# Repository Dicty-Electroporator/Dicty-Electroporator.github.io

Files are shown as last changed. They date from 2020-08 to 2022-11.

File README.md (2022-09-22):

<h2>
   <p><em>Dictyostelium</em> <em>discoideum</em> Electroporator</p>
</h2>
<p><a href="https://minhaskamal.github.io/DownGit/#/home?url=https://github.com/Dicty-Electroporator/Dicty-Electroporator.github.io/tree/Gen-2.1-with-edits/Dictyostelium%20discoideum%20Electroporator">Download Project</a></p>
<p>Easily constructed by investigators with no electronics knowledge, we present an inexpensive and open-source electroporation apparatus for <em>Dictyostelium discoideum</em> with all functional modules and peripherals from Cauchy et al., 2022, "A Low-cost Electroporator for Genetically Modifying Social Amoeba <em>Dictyostelium discoideum</em>" submitted to Journal of Open Hardware.</p>
<p><strong>Description:&nbsp;</strong>Electroporation to introduce DNA into cells is a common technique in genetic engineering. <em>Dictyostelium discoideum</em> is a well-established eukaryotic model organism that is frequently genetically modified (transformed). We present here an electroporator capable of high efficiency transformation. Our electroporator consists of a high voltage power supply, pulse generator circuit and cell sample cuvette chamber. The power supply is programmed to deliver desired voltage, which when activated by a double-pole, double-throw switch (DPDT) charges a capacitor. Further switching allows the charged capacitor to deliver a precise, consistent exponential decay wave of the proper duration to the cuvette containing a <em>D. discoideum</em> cell and DNA mixture. The high-voltage circuit is housed in an electrically insulated enclosure - we chose a plastic electrical junction box with appropriate holes for switch mounting and cables to pass. A 3D printable cuvette holder was designed and is available in .stl, .dwg and .iges formats. An inexpensive 1,000-volt digital multimeter was integrated into the design to aid in development and testing. To provide hands-free monitoring of the real-time capacitor voltage, we connected multimeter test leads to the capacitor poles. In addition to the standard build, we present here an alternative design for the pulse generator, which we will refer to as "modular". The standard pulse generator was designed to be durable for repeated use in multiple <em>D. discoideum</em> electroporation experiments. This design includes a soldered padboard with high power rated components. The modular pulse generator is designed for ease of build, is easily modified by swapping components for alternative waveforms, and is intended for a small number of electroporations and not routine or repeated use.</p>

<p><strong>License:&nbsp;</strong><a href="https://minhaskamal.github.io/DownGit/#/home?url=https://github.com/Dicty-Electroporator/Dicty-Electroporator.github.io/blob/Base/LICENSE">CERN Open Hardware License</a></p>
<p>&nbsp;</p> 
<h1>
   <p><em>D. discoideum</em> Electroporation System</p>
</h1>
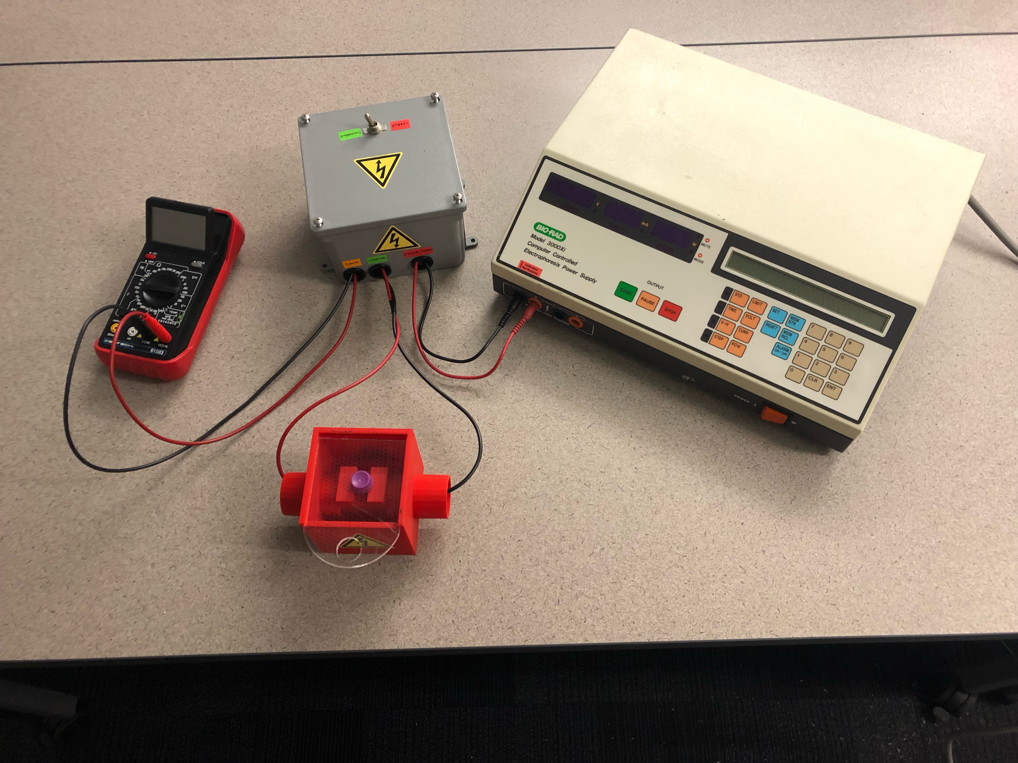
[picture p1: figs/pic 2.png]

<h2>
   <p>Standard Pulse Generator</p>
</h2>
<p>The pulse generator circuit features a soldered breadboard with high power components. Assembly is straightforward and can be constructed by a beginner with access to soldering equipment. The cuvette chamber features a built-in enclosure with limited access to the power connectors as well as a removable lid. The lid can be 3D printed or laser cut from a sheet of acrylic or other material. 3D design and print files are available on this page. We chose a biodegradable and fire-resistant 3D print media,  Polylactic acid (PLA). Other cost effective, readily available, and more durable print media are available. The system was tested and performs as efficiently as a commercial electroporator.</p>
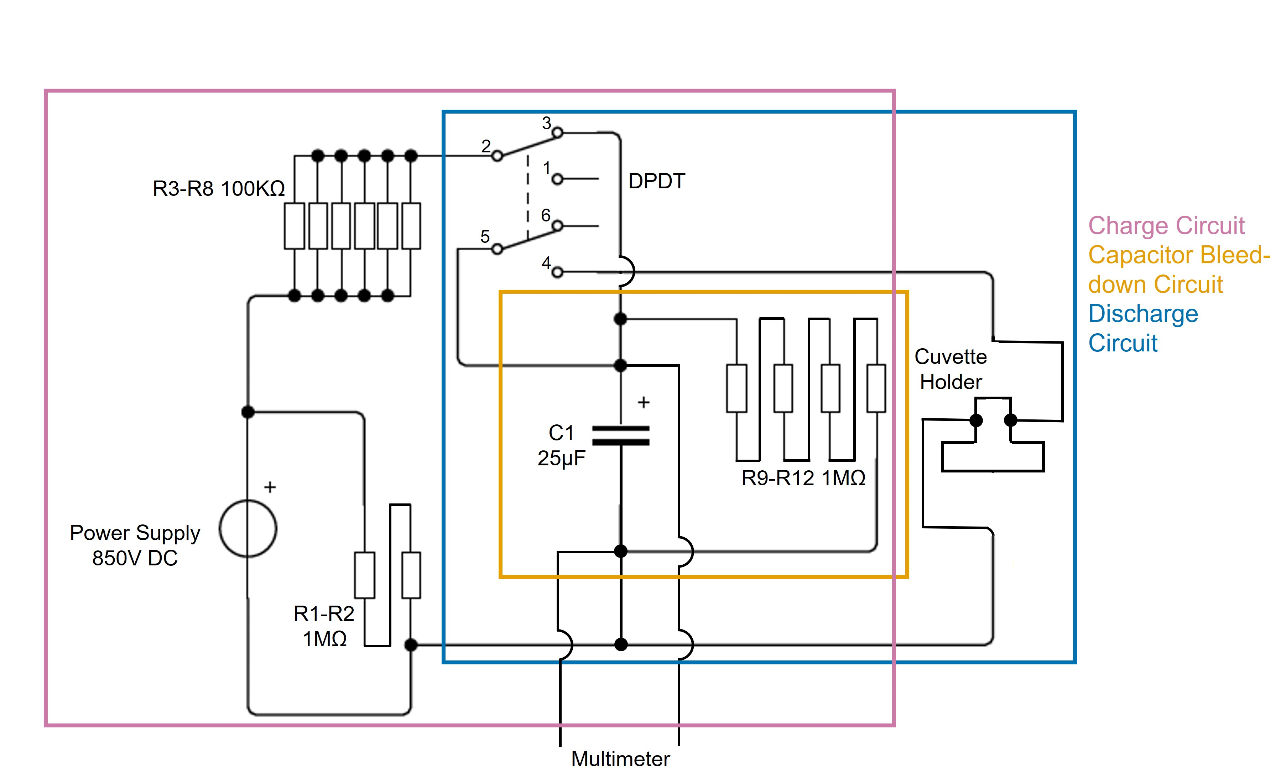
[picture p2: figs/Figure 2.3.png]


<p>2W (Watt)-1MΩ (Ohm) resistors were used for resistors R1-R2 and R9-R12. 8W-100kΩ resistors were used for resistors R3-R8.</p>
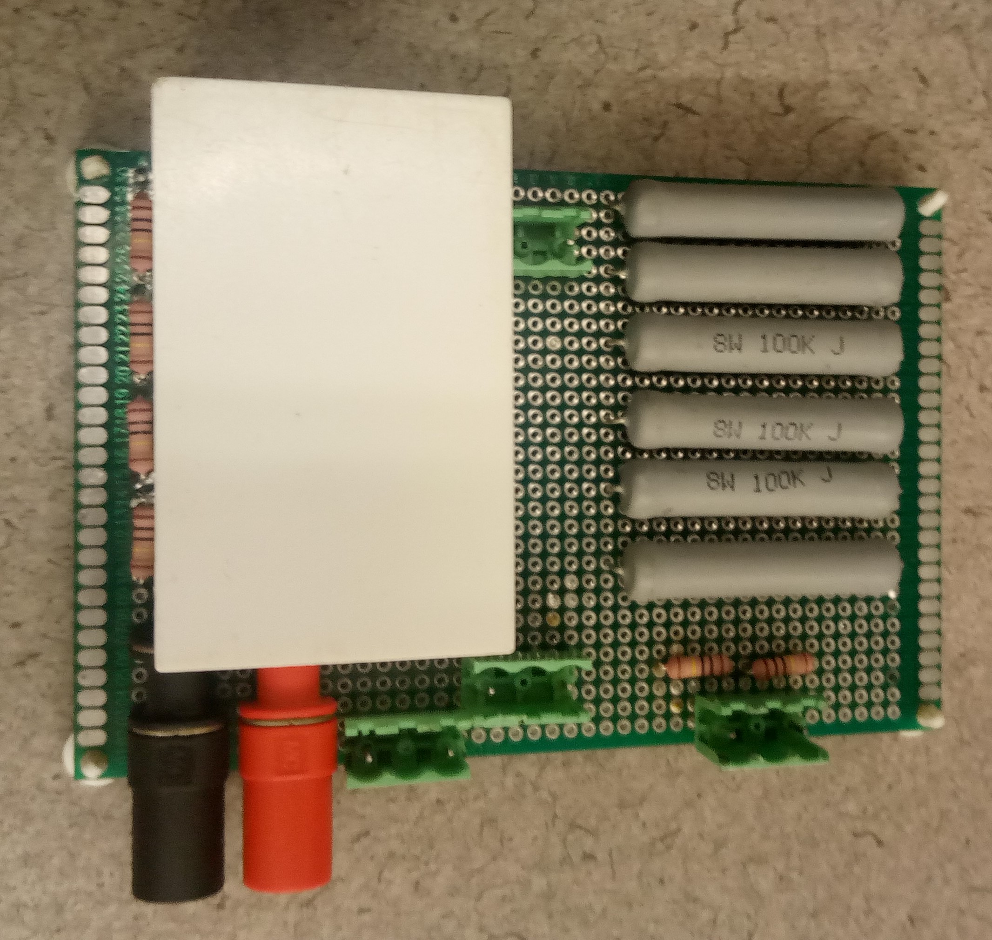
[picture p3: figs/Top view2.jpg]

<p>&nbsp;</p>
<p>Components were fixed to the breadboard using the long leads of resistors as traces on the underside of the 8cm x 12cm padboard.</p>
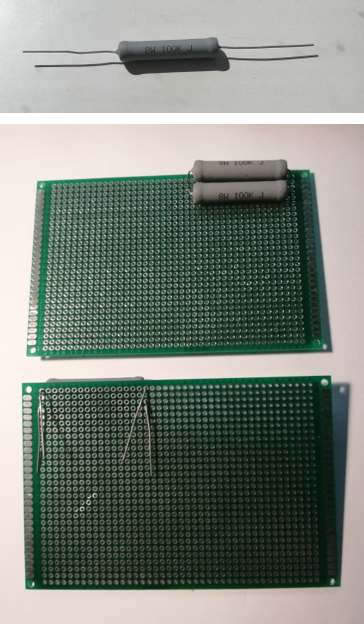
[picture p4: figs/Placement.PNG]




<p>Trimmed resistor terminals and solder were used to create traces. This layout accommodates the lack of premade traces found on solderless breadboards. In addition, banana jack connectors were soldered to the component side and traced to the opposing capacitor poles at each end of the bleed-down resistor array. This allows connection to a multimeter and real-time monitoring of the capacitor voltage during electroporation and provides assurance the capacitor is safe.</p>
<h2>
   <p>Enclosure</p>
</h2>
<p>We chose a commercially available plastic junction box to enclose our pulse generator circuit. A 13mm hole was drilled into the enclosure cover for the DPDT and 22mm holes were marked and drilled in the enclosure which provided a nice fit for the plastic NM connectors and pass-through cables.</p>
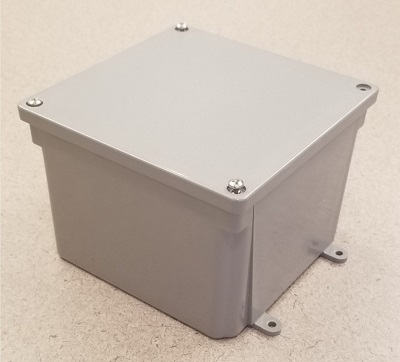
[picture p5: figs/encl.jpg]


<h4>
   <p>Assembly instruction</p>
</h4>
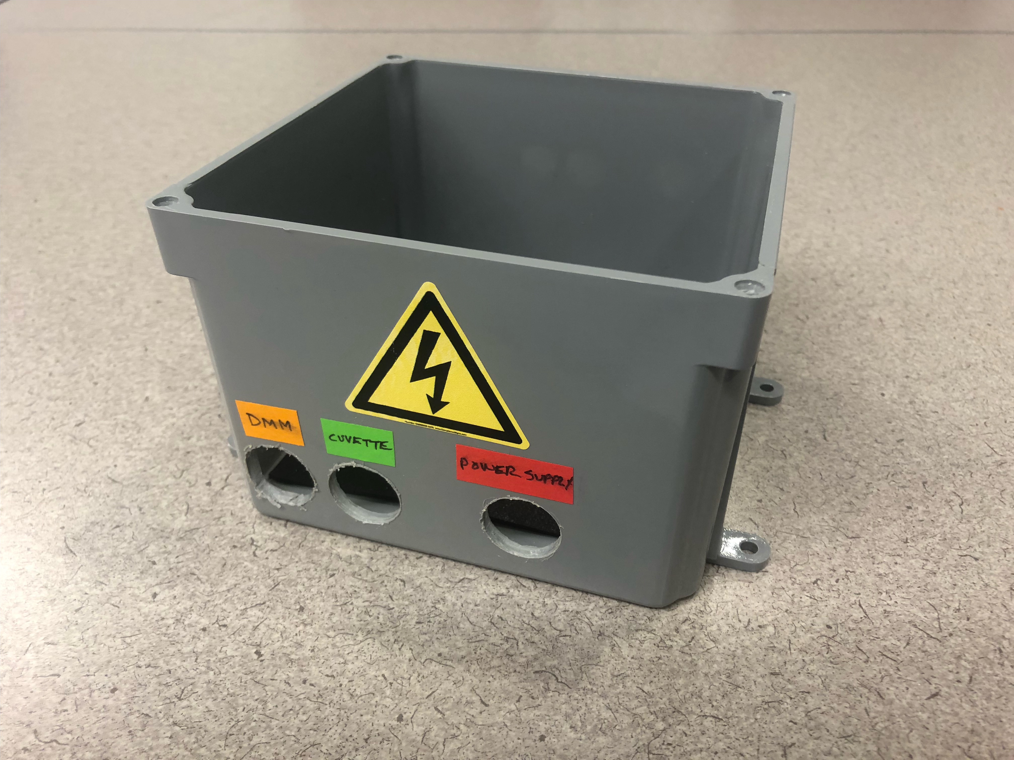
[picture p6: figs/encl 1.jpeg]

<p>Drill three 22mm holes in any side of the enclosure. Label the holes as shown. DMM above refers to digital multimeter.</p>
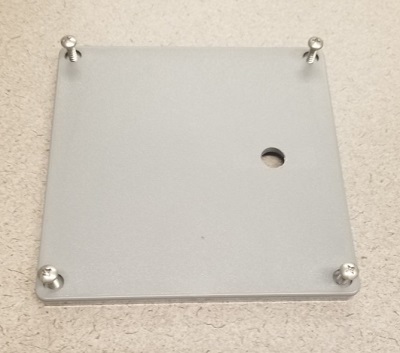
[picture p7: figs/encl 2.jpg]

<p>Drill 13mm hole in enclosure lid for switch mounting. Place the hole where hand-switching will be most comfortable.</p>
<p>&nbsp;</p>
<h3>
   <p>Switch wiring</p>
</h3>
<p>&nbsp;</p>
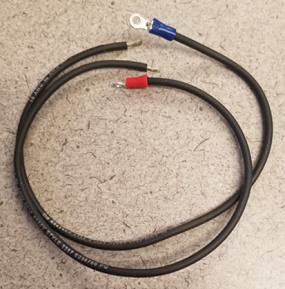
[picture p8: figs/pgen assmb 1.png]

<p>Cut 4 pieces of 18 AWG wire (for the switch) to 30cm lengths and strip approx. 5mm of bare wire from each end. Crimp one end of each wire to a ring terminal.</p>
<p>&nbsp;</p>
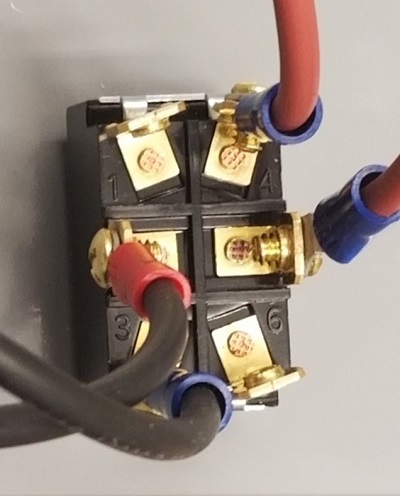
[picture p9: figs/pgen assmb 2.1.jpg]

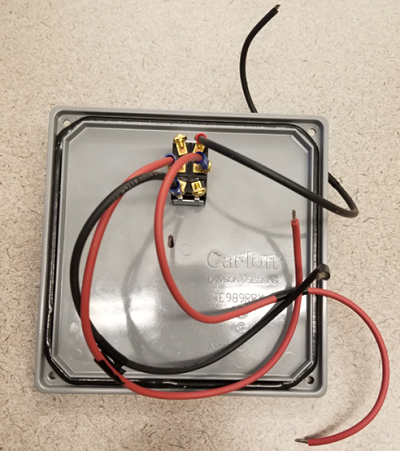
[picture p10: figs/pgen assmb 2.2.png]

<p>Attach ring terminals (with wire from step 1) to terminals 2, 3, 4, and 5 of the DPDT switch. Install switch into hole drilled into lid of case.</p>
<p>&nbsp;</p>
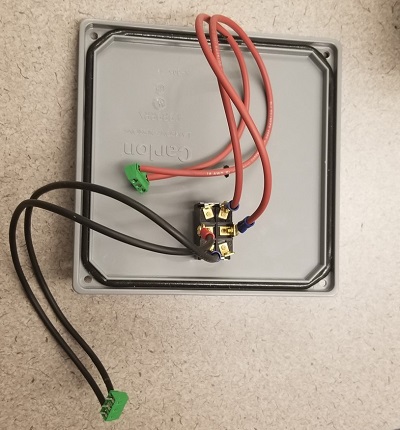
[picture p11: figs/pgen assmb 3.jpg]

<p>Using the 4 pieces of 18 AWG wire with ring terminals from step 1, connect switch terminals 2 and 3 to the outboard ports of one terminal block and 4 and 5 to the outboard ports of another terminal block. Insert paired wires into outside wire cages of terminal blocks, then tighten terminal block screws.</p>
<p>&nbsp;</p>
<h2>
   <p>Cuvette Chamber</p>
</h2>
<p>The cuvette chamber provides the delivery vehicle for the electric field that causes electroporation. The cuvette chamber was designed to keep inward pressure on the plug ends that contact the cuvette. Hands-free electroporation was an important consideration in our design. The built-in spring-like nature of the resulting connection ensures constant contact when like charges build up on each plug and its corresponding cuvette contact. It is also notable that we chose stackable banana plugs so that we could tandem a 1,000V multimeter to the cuvette holder; especially useful during pre-electroporation functions check.</p>

<p>The cuvette chamber has several safety features. It is enclosed in a four-sided box with a removable lid that can be laser cut from a clear Poly acrylic sheet or 3D printed. Collars around lead connectors provide protection from shock exposure. Design and print files are included below. The chamber can be printed with various levels of fill; 15% fill is shown here and functioned well in our hands.</p>
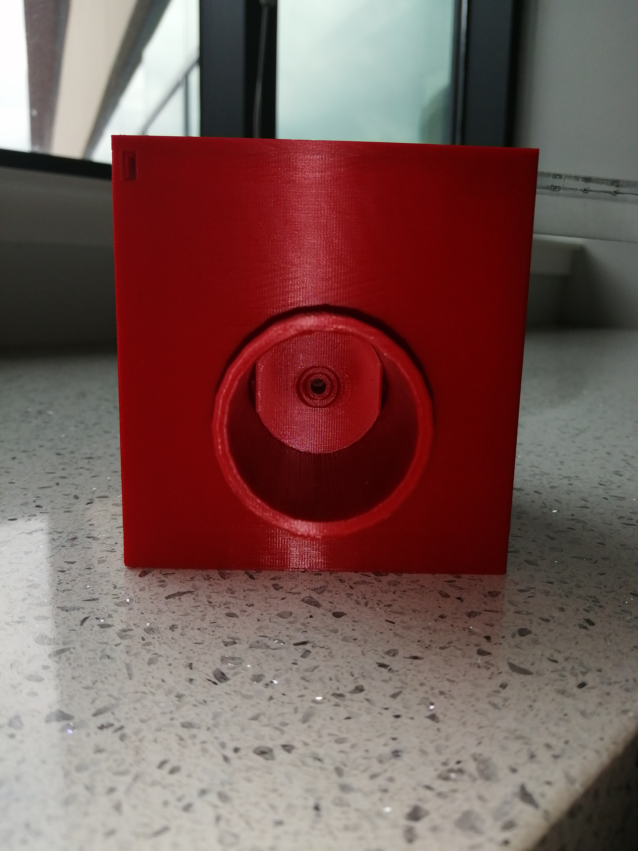
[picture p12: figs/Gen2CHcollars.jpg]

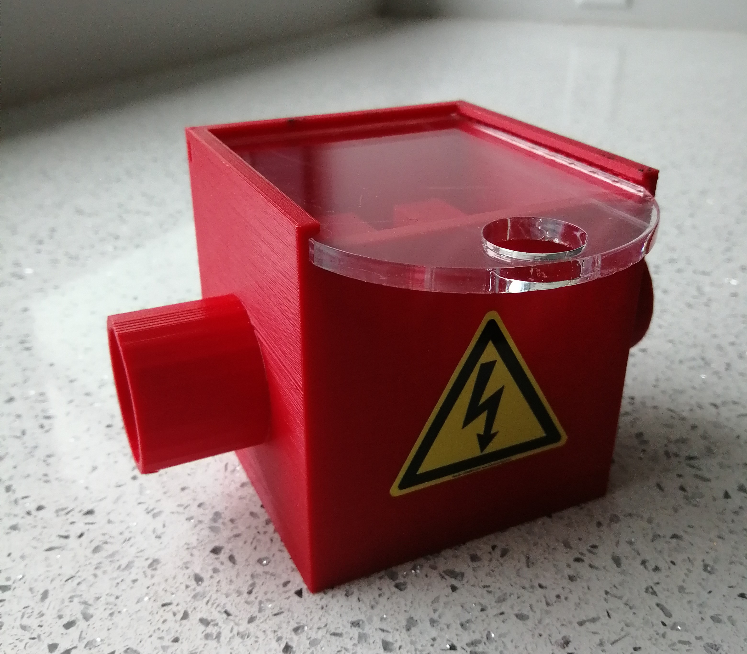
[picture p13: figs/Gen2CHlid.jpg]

<p><strong>Print File:&nbsp;<a href="https://github.com/Dicty-Electroporator/Dicty-Electroporator.github.io/raw/Gen-2.1-with-edits/Enhanced%20Cuvette%20Chamber%203DPrintSTL.stl">Cuvette Chamber.stl</a></strong></p>
<p><strong>CAD Design File:&nbsp;<a href="https://github.com/Dicty-Electroporator/Dicty-Electroporator.github.io/raw/Gen-2.1-with-edits/Enhanced%20Cuvette%20Chamber%20CAD.dwg">Cuvette Chamber CAD.dwg</a></strong></p>
<p><strong>IGES File:&nbsp;<a href="https://minhaskamal.github.io/DownGit/#/home?url=https://github.com/Dicty-Electroporator/Dicty-Electroporator.github.io/blob/Gen-2.1-with-edits/Dictyostelium%20discoideum%20Electroporator/Enclosure%20Lid%20FreeCAD.iges">Cuvette Chamber.iges</a></strong></p>

<p><strong>Chamber Lid Laser Cut File:&nbsp;<a href="https://github.com/Dicty-Electroporator/Dicty-Electroporator.github.io/raw/Gen-2.1-with-edits/Enclosure%20Lid%20LaserCutSVG.svg">Chamber Lid.SVG</a></strong></p>
<p><strong>Chamber Lid Print File:&nbsp;<a href="https://github.com/Dicty-Electroporator/Dicty-Electroporator.github.io/raw/Gen-2.1-with-edits/Enclosure%20Lid%20STL.stl">Chamber Lid STL.stl</a></strong></p>
<p><strong>Chamber Lid CAD Design File:&nbsp;<a href="https://github.com/Dicty-Electroporator/Dicty-Electroporator.github.io/raw/Gen-2.1-with-edits/Enclosure%20Lid%20CAD.dwg">Chamber Lid CAD.dwg</a></strong></p>

<p><strong>Chamber Lid IGES File:&nbsp;<a href="https://minhaskamal.github.io/DownGit/#/home?url=https://github.com/Dicty-Electroporator/Dicty-Electroporator.github.io/blob/Gen-2.1-with-edits/Dictyostelium%20discoideum%20Electroporator/Enhanced%20Cuvette%20Chamber%20FreeCAD.iges">Chamber Lid.iges</a></strong></p>
<p>Note: IGES drawing files save vector image data to transfer information between different CAD applications. Graphics acceleration may have to be disabled in order for some open source CAD software to load.</p>
<p>&nbsp;</p>
<h2>
   <p>Bill of Materials</p>
</h2>
<table>
   <thead>
      <tr>
         <td>
            <p><strong>Part</strong></p>
         </td>
         <td>
            <p><strong>Quantity</strong></p>
         </td>
         <td>
            <p><strong>Supplier</strong></p>
         </td>
         <td>
            <p><strong>Supplier part number</strong></p>
         </td>
         <td>
            <p><strong>URL</strong></p>
         </td>
      </tr>
   </thead>
   <tbody>
      <tr>
         <td>
            <p>Power supply banana plug test leads</p>
         </td>
         <td>
            <p>2</p>
         </td>
         <td>
            <p>Mouser</p>
         </td>
         <td>
            <p>4911A-60/4911A-62</p>
         </td>
         <td>
            <p><a href="https://www.mouser.com/Search/Refine?Keyword=4911a-60">www.mouser.com</a></p>
         </td>
      </tr>
          <tr>
         <td>
            <p>Test Lead Wire 25 in. red</p>
         </td>
         <td>
            <p>1</p>
         </td>
         <td>
            <p>Powerwerx</p>
         </td>
         <td>
            <p>Wire-TL-18-00-25</p>
         </td>
         <td>
            <p><a href="https://powerwerx.com/test-lead-rubber-flexible-wire">powerwerx.com</a></p>
         </td>
      </tr>
      <tr>
         <td>
            <p>Test Lead Wire 25 in. black</p>
         </td>
         <td>
            <p>1</p>
         </td>
         <td>
            <p>Powerwerx</p>
         </td>
         <td>
            <p>Wire-TL-18-00-25</p>
         </td>
         <td>
            <p><a href="https://powerwerx.com/test-lead-rubber-flexible-wire">powerwerx.com</a></p>
         </td>
      </tr>
      <tr>
         <td>
            <p>PCB Prototype padboard - 8cm x 12cm</p>
         </td>
         <td>
            <p>1</p>
         </td>
         <td>
            <p>Amazon</p>
         </td>
         <td>
            <p>739340318574</p>
         </td>
         <td>
            <p><a href="https://www.amazon.com/gp/product/B07Y3DVM1W/ref=ppx_yo_dt_b_asin_title_o05_s00?ie=UTF8&psc=1">www.amazon.com</a></p>
         </td>
      </tr>
      <tr>
         <td>
            <p>Resistors - 8W-100kΩ</p>
         </td>
         <td>
            <p>6</p>
         </td>
         <td>
            <p>Mouser</p>
         </td>
         <td>
            <p>279-ROX8J100K</p>
         </td>
         <td>
            <p><a href="https://www.mouser.com/ProductDetail/TE-Connectivity-Holsworthy/ROX8J100K?qs=gZXFycFWdAMYKZPoGrub8g%3D%3D">www.mouser.com</a></p>
         </td>
      </tr>
      <tr>
         <td>
            <p>Resistors - 2W-1MΩ</p>
         </td>
         <td>
            <p>6</p>
         </td>
         <td>
            <p>Mouser</p>
         </td>
         <td>
            <p>594-5083NW1M000J</p>
         </td>
         <td>
            <p><a href="https://www.mouser.com/ProductDetail/Vishay-BC-Components/PR02000201004JR500?qs=LCMWAU1DZcwmgZ1lvVsGww%3D%3D">www.mouser.com</a></p>
         </td>
      </tr>
      <tr>
         <td>
            <p>Bio-Rad Model 3000xi Computer Controlled Electrophoresis Power Supply (or similar capable of generating at least 1KV DC)</p>
         </td>
         <td>
            <p>1</p>
         </td>
         <td>
            <p>ebay or other supplier of used scientific equipment</p>
         </td>
         <td>
            
         </td>
         <td>
            <p><a href="https://www.ebay.com">www.ebay.com</a></p>
         </td>
      </tr>
      <tr>
         <td>
            <p>3-Pin 5.08mm Pitch Male Female Plug-in PCB Screw Terminal Block Connector</p>
         </td>
         <td>
            <p>2</p>
         </td>
         <td>
            <p>Amazon</p>
         </td>
         <td>
            <p>0766832280286</p>
         </td>
         <td>
            <p><a href="https://www.amazon.com/PoiLee-5-08mm-Female-Terminal-Connector/dp/B07TQLYQ7W/ref=asc_df_B07TQLYQ7W/?tag=hyprod-20&linkCode=df0&hvadid=385629037133&hvpos=&hvnetw=g&hvrand=8172029133657464055&hvpone=&hvptwo=&hvqmt=&hvdev=c&hvdvcmdl=&hvlocint=&hvlocphy=9005131&hvtargid=pla-846156762614&psc=1&tag=&ref=&adgrpid=73872201970&hvpone=&hvptwo=&hvadid=385629037133&hvpos=&hvnetw=g&hvrand=8172029133657464055&hvqmt=&hvdev=c&hvdvcmdl=&hvlocint=&hvlocphy=9005131&hvtargid=pla-846156762614">www.amazon.com</a></p>
         </td>
      </tr>
      <tr>
         <td>
            <p>3-Position Screw Terminal Block</p>
         </td>
         <td>
            <p>2</p>
         </td>
         <td>
            <p>Addicore</p>
         </td>
         <td>
            <p>AD305</p>
         </td>
         <td>
            <p><a href="https://www.addicore.com/3-Position-Screw-Terminal-Block-p/ad305.htm">www.addicore.com</a></p>
         </td>
      </tr>
      <tr>
         <td>
            <p>Male-Male fixed length jumper wires</p>
         </td>
         <td>
            <p>5</p>
         </td>
         <td>
            <p>Jameco</p>
         </td>
         <td>
            <p>2127718</p>
         </td>
         <td>
            <p><a href="https://www.jameco.com/z/WJW-70B-5-70-Piece-Jumper-Wire-Kit-22AWG-14-Lengths-10-Colors_2127718.html">www.jameco.com</a></p>
         </td>
      </tr>

      <tr>
         <td>
            <p>Capacitor - 25μF - 1,300V</p>
         </td>
         <td>
            <p>1</p>
         </td>
         <td>
            <p>Mouser</p>
         </td>
         <td>
            <p>C4AQUBW5250A3NJ</p>
         </td>
         <td>
            <p><a href="https://www.mouser.com/ProductDetail/KEMET/C4AQUBW5250A3NJ?qs=%2Fha2pyFadugKSuBjMOjke5u9ridkq4YeClSJSpnddrBZ2GZPnEOejQ%3D%3D">www.mouser.com</a></p>
         </td>
      </tr>

      <tr>
         <td>
            <p>Ring Terminals</p>
         </td>
         <td>
            <p>4</p>
         </td>
         <td>
            <p>Lowes</p>
         </td>
         <td>
            <p>136093</p>
         </td>
         <td>
            <p><a href="https://www.lowes.com/pd/Utilitech-20-Count-Ring-Wire-Connectors/999953294">www.lowes.com</a></p>
         </td>
      </tr>

      <tr>
         <td>
            <p>DPDT toggle switch - 20A</p>
         </td>
         <td>
            <p>1</p>
         </td>
         <td>
            <p>Ace Hardware</p>
         </td>
         <td>
            <p>GSW-16</p>
         </td>
         <td>
            <p><a href="https://www.acehardware.com/departments/lighting-and-electrical/switches-outlets-and-plugs/switches/3531324">www.acehardware.com</a></p>
         </td>
      </tr>
      <tr>
         <td>
            <p>3/8-in Plastic NM Connector</p>
         </td>
         <td>
            <p>2</p>
         </td>
         <td>
            <p>Lowes</p>
         </td>
         <td>
            <p>44740</p>
         </td>
         <td>
            <p><a href="https://www.lowes.com/pd/Sigma-Electric-ProConnex-3-8-in-Snap-in-Connector-Conduit-Fitting/3151125">www.lowes.com</a></p>
         </td>
      </tr>
      <tr>
         <td>
            <p>Junction box</p>
         </td>
         <td>
            <p>1</p>
         </td>
         <td>
            <p>Lowes</p>
         </td>
         <td>
            <p>10029</p>
         </td>
         <td>
            <p><a href="https://www.lowes.com/pd/CANTEX-Junction-Box-Gang-Gray-Plastic-Weatherproof-New-Work-Old-Work-Standard-Square-Interior-Exterior-Electrical-Box/3276255">www.lowes.com</a></p>
         </td>
      </tr>
      <tr>
         <td>
            <p>3D printed cuvette holder</p>
         </td>
         <td>
            <p>1</p>
         </td>
         <td>&nbsp;</td>
         <td>&nbsp;</td>
         <td>&nbsp;</td>
      </tr>
      <tr>
         <td>
            <p>1kV Multimeter</p>
         </td>
         <td>
            <p>1</p>
         </td>
         <td>
            <p>CEN-TECH (or similar)</p>
         </td>
         <td>
            <p>61593/P37772</p>
         </td>
         <td>
            <p><a href="https://www.harborfreight.com/11-function-digital-multimeter-with-audible-continuity-61593.html">www.harborfreight.com</a></p>
         </td>
      </tr>

      <tr>
         <td>
            <p>Banana Jack Connector Standard Banana Solder Red/Black</p>
         </td>
         <td>
            <p>2</p>
         </td>
         <td>
            <p>Digi-Key</p>
         </td>
         <td>
            <p>3185-FCR7350R-ND (or similar)</p>
         </td>
         <td>
            <p><a href="https://www.digikey.com/en/products/detail/cliff-electronic-components-ltd/FCR7350R/13588710?utm_adgroup=Banana%20and%20Tip%20Connectors%20-%20Jacks%2C%20Plugs&utm_source=google&utm_medium=cpc&utm_campaign=Shopping_Product_Connectors%2C%20Interconnects_NEW&utm_term=&utm_content=Banana%20and%20Tip%20Connectors%20-%20Jacks%2C%20Plugs&gclid=Cj0KCQjwxIOXBhCrARIsAL1QFCaS0i6JGg6UL4RwvlMztOWSG87LscZ9CT0JJhaYllfI620GVLvLvh8aAoXKEALw_wcB">www.digikey.com</a></p>
         </td>
         </tr>
            <tr>
         <td>
            <p>ISO-3864 Warning Symbol Labels - High Voltage</p>
         </td>
         <td>
            <p>1x5</p>
         </td>
         <td>
            <p>emedco</p>
         </td>
         <td>
            <p>SYM28R71VAD</p>
         </td>
         <td>
            <p><a href="https://www.emedco.com/iso-warning-symbol-labels-high-voltage-sym28.html?utm_campaign=PC-02-Labels_CatchAllSmartShopping_Emedco_PLA_NB_C_Google_US&utm_source=google&utm_medium=cpc&utm_term=&matchtype=&device=c&adgroupid=Catch+All+-+Old+Hierarchy&gclid=CjwKCAjwu5yYBhAjEiwAKXk_eOuXOPUcWMaTqpkfMpD0W6rF3nKtdNauUNZsvvMGXhg1-YWTsYK_4RoCVK8QAvD_BwE&gclsrc=aw.ds#SYM28R71VAD">www.emedco.com</a></p>
         </td>
         </tr>
   </tbody>
</table>

<p>&nbsp;</p> 
<h1>
   <p>Modular Pulse Generator</p>
</h1>
<p>Components and configurations of the electrical circuit are described here. For all connections, refer to the circuit diagram and photos of the assembled circuit.</p>
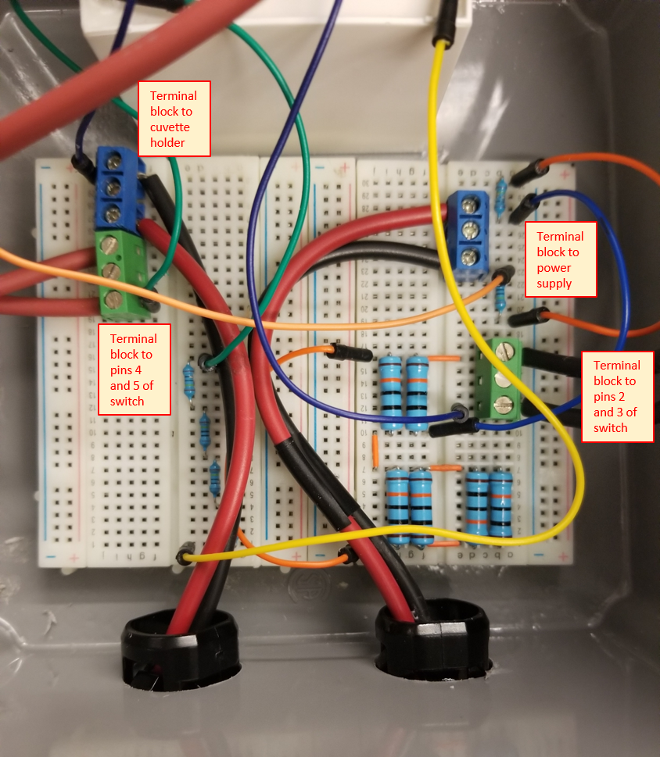
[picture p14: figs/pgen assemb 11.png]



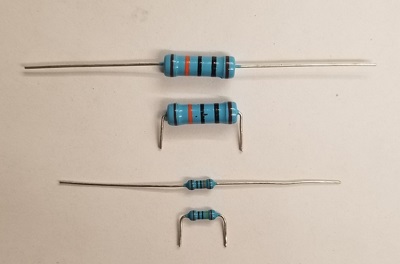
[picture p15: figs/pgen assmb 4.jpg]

<p>Clip resistor pins and bend at 90-degree angle to fit into breadboard terminals.</p>
<p>&nbsp;</p>
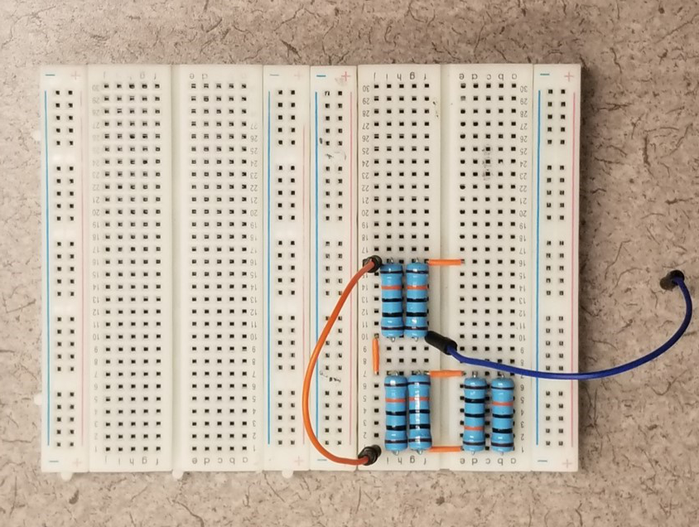
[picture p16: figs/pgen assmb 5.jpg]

<p>Connect six 100KΩ - 2W resistors (R3-R8) in parallel into breadboards using jumper wires as needed to form connections.</p>
<p>&nbsp;</p>
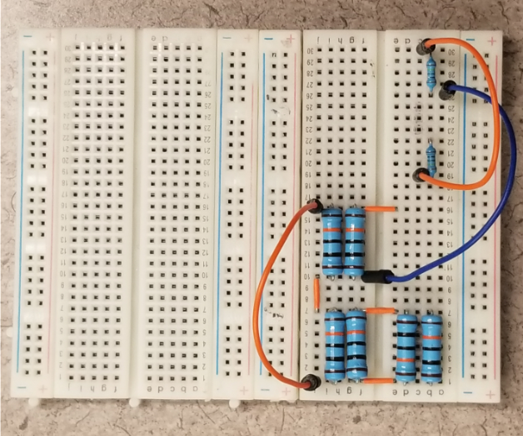
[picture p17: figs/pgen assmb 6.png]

<p>Connect two 1MΩ - 1/2W resistors (R1 and R2) in series into breadboards using jumper wires as needed to form connections.</p>
<p>&nbsp;</p>
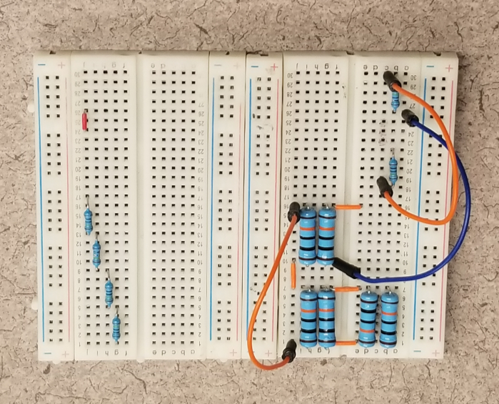
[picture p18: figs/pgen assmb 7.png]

<p>Connect four 1MΩ - 1/2W resistors (R9-R12) in series. A short jumper wire is also placed on the board as shown (upper left section of breadboard) that will become a link between the terminal blocks connecting switch position four and the cuvette chamber.</p>
<p>&nbsp;</p>
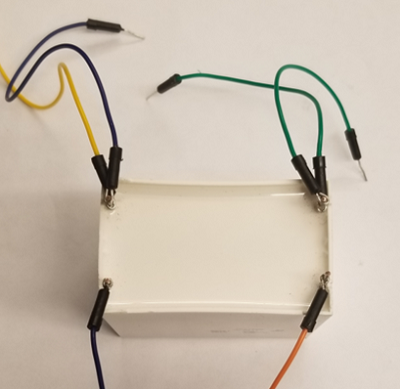
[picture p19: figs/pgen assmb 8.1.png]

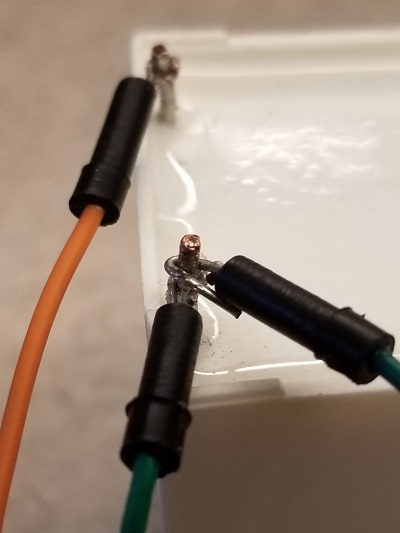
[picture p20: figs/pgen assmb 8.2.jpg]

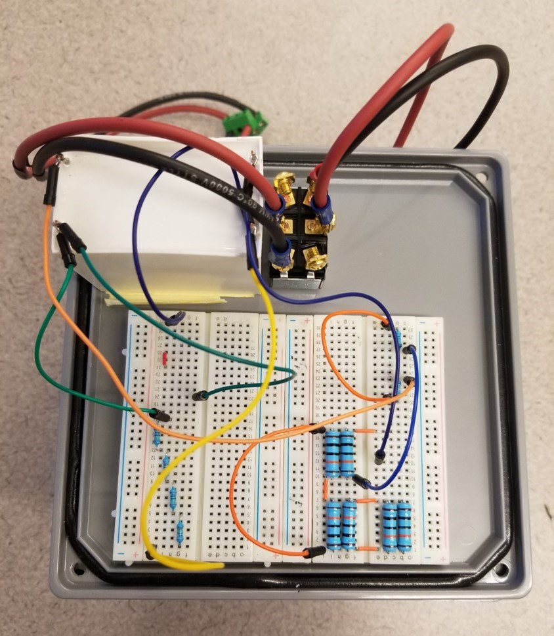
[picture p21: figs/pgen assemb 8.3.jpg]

<p>Ensure the 25μF - 1,300V capacitor is not charged before handling by measuring voltage across the terminals using the multimeter. Connect three 20cm flexible jumper wires to each pole of the capacitor. Note that two leads from each capacitor pole are present. Wire terminals can be crimped around capacitor leads or soldered for establishing a more permanent connection. Attach capacitor leads to the breadboard per circuit diagram and accompanying photos.</p>
<p>&nbsp;</p>
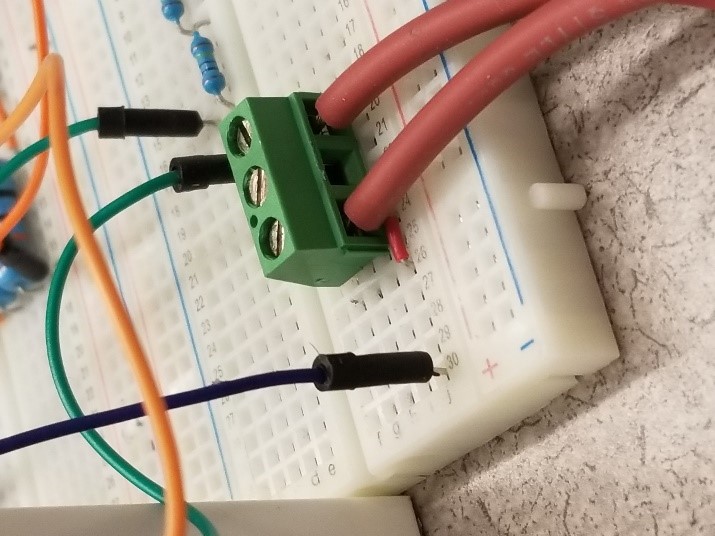
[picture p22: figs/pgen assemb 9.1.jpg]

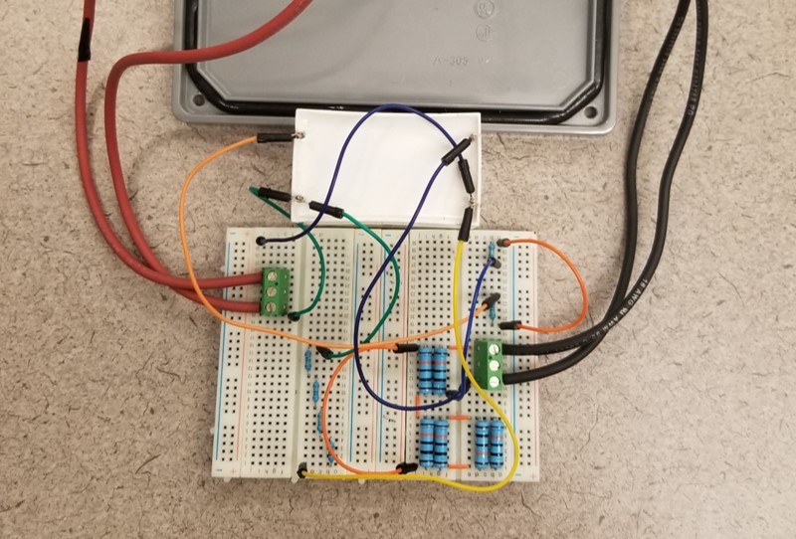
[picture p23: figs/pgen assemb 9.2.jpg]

<p>Connect terminal blocks from switch leads to the breadboard.</p>
<p>&nbsp;</p>
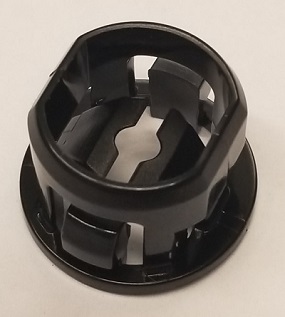
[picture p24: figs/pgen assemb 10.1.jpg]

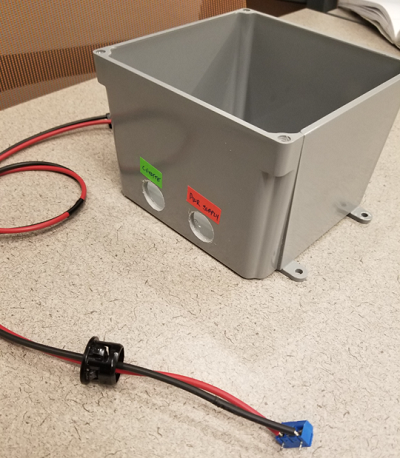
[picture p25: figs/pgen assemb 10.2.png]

<p>Cut one red and one black 60 in. test lead in half. Strip ends to leave approximately 5mm of bare wire. It might be helpful to tape the two pairs of one red and one black wire together every few centimeters. Pass stripped wire ends through NM plastic connectors about 10cm. Connect terminal blocks to the stripped ends by inserting paired wires into outside wire cages of terminal blocks, then tighten terminal block screws. Push NM plastic connectors into the cable pass-through holes of the enclosure (note that only two 22mm holes need to be made in the modular pulse generator enclosure, compared to three in the standard pulse generator enclosure).</p>
<p>&nbsp;</p>

<p>Pull the terminal block ends of the power supply and cuvette holder cables further through the pass-through holes with only sufficient play to insert the terminal blocks into the appropriate places on the breadboards.</p>
<p>&nbsp;</p>
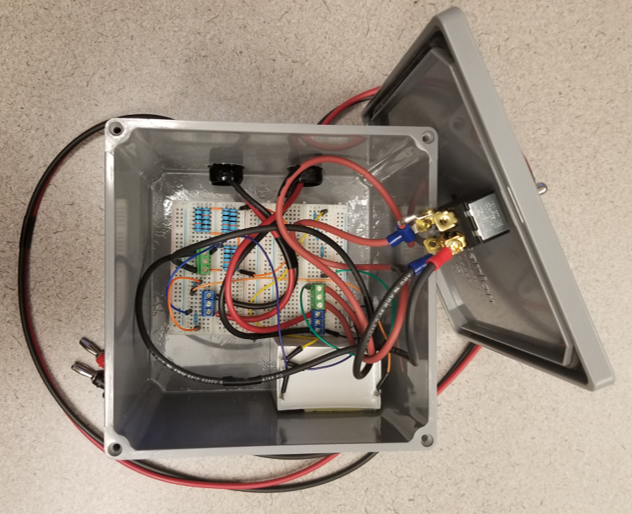
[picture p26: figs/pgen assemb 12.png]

<p>Adhere the breadboards and capacitor to the inside base of the enclosure. While we used 2-sided tape, glue could be used for a more permanent solution. Connect power supply and cuvette holder terminal blocks to the breadboard.</p>
<p>&nbsp;</p>
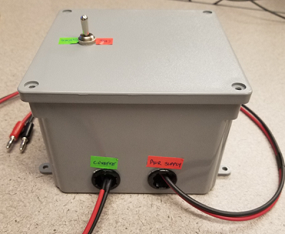
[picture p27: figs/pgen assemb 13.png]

<p>Attach enclosure cover.</p>
<p>&nbsp;</p>

<h2>
   <p>Bill of Materials</p>
</h2>
<table>
   <thead>
      <tr>
         <td>
            <p><strong>Part</strong></p>
         </td>
         <td>
            <p><strong>Quantity</strong></p>
         </td>
         <td>
            <p><strong>Supplier</strong></p>
         </td>
         <td>
            <p><strong>Supplier part number</strong></p>
         </td>
         <td>
            <p><strong>URL</strong></p>
         </td>
      </tr>
   </thead>
   <tbody>
      <tr>
         <td>
            <p>400 Point solderless breadboard</p>
         </td>
         <td>
            <p>2</p>
         </td>
         <td>
            <p>Jameco</p>
         </td>
         <td>
            <p>20601</p>
         </td>
         <td>
            <p><a href="[http://www.jameco.com](https://www.jameco.com/z/WBU-301-R-Jameco-Valuepro-400-Point-Solderless-Breadboard-3-3-Lx2-1-W_20601.html)">www.jameco.com</a></p>
         </td>
      </tr>
      <tr>
         <td>
            <p>Male-Male fixed length jumper wires</p>
         </td>
         <td>
            <p>1</p>
         </td>
         <td>
            <p>Jameco</p>
         </td>
         <td>
            <p>2127718</p>
         </td>
         <td>
            <p><a href="https://www.jameco.com/z/WJW-70B-5-70-Piece-Jumper-Wire-Kit-22AWG-14-Lengths-10-Colors_2127718.html">www.jameco.com</a></p>
         </td>
      </tr>
      <tr>
         <td>
            <p>Test Lead Wire 25 in. red</p>
         </td>
         <td>
            <p>1</p>
         </td>
         <td>
            <p>Powerwerx</p>
         </td>
         <td>
            <p>Wire-TL-18-00-25</p>
         </td>
         <td>
            <p><a href="https://powerwerx.com/test-lead-rubber-flexible-wire">powerwerx.com</a></p>
         </td>
      </tr>
      <tr>
         <td>
            <p>Test Lead Wire 25 in. black</p>
         </td>
         <td>
            <p>1</p>
         </td>
         <td>
            <p>Powerwerx</p>
         </td>
         <td>
            <p>Wire-TL-18-00-25</p>
         </td>
         <td>
            <p><a href="https://powerwerx.com/test-lead-rubber-flexible-wire">powerwerx.com</a></p>
         </td>
      </tr>
      <tr>
         <td>
            <p>Male-Male flexible jumper wires</p>
         </td>
         <td>
            <p>1</p>
         </td>
         <td>
            <p>Walmart</p>
         </td>
         <td>
            <p>NA</p>
         </td>
         <td>
            <p><a href="[https://www.mouser.com/ProductDetail/BusBoard-Prototype-Systems/KIT-ZWx4?qs=sGAEpiMZZMvh1pRuiUVjFZ0aAJXGPyuNDJiA5Z8ZR2Q%2FfInvTU3aKA%3D%3D](https://www.walmart.com/ip/Jumpers-Wire-Kit-Breadboard-Jumper-Assorted-Length-Brass-Wire-Core-Durable-For-Connecting-Electronic-Components/1240167396?wmlspartner=wlpa&selectedSellerId=101092147)">www.walmart.com</a></p>
         </td>
      </tr>
      <tr>
         <td>
            <p>Capacitor - 25μF - 1,300V</p>
         </td>
         <td>
            <p>1</p>
         </td>
         <td>
            <p>Mouser</p>
         </td>
         <td>
            <p>C4AQUBW5250A3NJ</p>
         </td>
         <td>
            <p><a href="https://www.mouser.com/ProductDetail/KEMET/C4AQUBW5250A3NJ?qs=%2Fha2pyFadugKSuBjMOjke5u9ridkq4YeClSJSpnddrBZ2GZPnEOejQ%3D%3D">www.mouser.com</a></p>
         </td>
      </tr>
      <tr>
         <td>
            <p>Red banana plug test lead - 60 inch</p>
         </td>
         <td>
            <p>1</p>
         </td>
         <td>
            <p>Mouser</p>
         </td>
         <td>
            <p>B-60-2</p>
         </td>
         <td>
            <p><a href="https://www.mouser.com/ProductDetail/Pomona-Electronics/B-60-2?qs=sGAEpiMZZMv8kklI404QlQaMEaX1aQ14">www.mouser.com</a></p>
         </td>
      </tr>
      <tr>
         <td>
            <p>Black banana plug test lead - 60 inch</p>
         </td>
         <td>
            <p>1</p>
         </td>
         <td>
            <p>Mouser</p>
         </td>
         <td>
            <p>B-60-0</p>
         </td>
         <td>
            <p><a href="https://www.mouser.com/ProductDetail/Pomona-Electronics/B-60-0?qs=sGAEpiMZZMv8kklI404QlV4QPmgLmIZb">www.mouser.com</a></p>
         </td>
      </tr>
      <tr>
         <td>
            <p>Ring Terminals</p>
         </td>
         <td>
            <p>4</p>
         </td>
         <td>
            <p>Lowes</p>
         </td>
         <td>
            <p>136093</p>
         </td>
         <td>
            <p><a href="https://www.lowes.com/pd/Utilitech-20-Count-Ring-Wire-Connectors/999953294">www.lowes.com</a></p>
         </td>
      </tr>
      <tr>
         <td>
            <p>Resistor - 1MΩ - 500mW</p>
         </td>
         <td>
            <p>6</p>
         </td>
         <td>
            <p>Mouser</p>
         </td>
         <td>
            <p>71-CMF551M0000BHEK</p>
         </td>
         <td>
            <p><a href="https://www.mouser.com/ProductDetail/Vishay-Dale/CMF551M0000BHEK?qs=rMX6kfwPG0qbAzHtP4OjAA%3D%3D">www.mouser.com</a></p>
         </td>
      </tr>
      <tr>
         <td>
            <p>Resistor - 100kΩ - 2W</p>
         </td>
         <td>
            <p>6</p>
         </td>
         <td>
            <p>Mouser</p>
         </td>
         <td>
            <p>603-MFR200FRF52-100K</p>
         </td>
         <td>
            <p><a href="[https://www.amazon.com/BAEASU-60PCS-Metal-Film-Resistor/dp/B07VCDJR8W?th=1](https://www.mouser.com/ProductDetail/YAGEO/MFR200FRF52-100K?qs=sGAEpiMZZMtlubZbdhIBIOunD5kldQoz6RmiTa0f1D8%3D)">www.mouser.com</a></p>
         </td>
      </tr>
      <tr>
         <td>
            <p>3-Position Screw Terminal Block</p>
         </td>
         <td>
            <p>4</p>
         </td>
         <td>
            <p>Addicore</p>
         </td>
         <td>
            <p>AD305</p>
         </td>
         <td>
            <p><a href="https://www.addicore.com/3-Position-Screw-Terminal-Block-p/ad305.htm">www.addicore.com</a></p>
         </td>
      </tr>
      <tr>
         <td>
            <p>DPDT toggle switch - 20A</p>
         </td>
         <td>
            <p>1</p>
         </td>
         <td>
            <p>Ace Hardware</p>
         </td>
         <td>
            <p>GSW-16</p>
         </td>
         <td>
            <p><a href="https://www.acehardware.com/departments/lighting-and-electrical/switches-outlets-and-plugs/switches/3531324">www.acehardware.com</a></p>
         </td>
      </tr>
      <tr>
         <td>
            <p>3/8-in Plastic NM Connector</p>
         </td>
         <td>
            <p>2</p>
         </td>
         <td>
            <p>Lowes</p>
         </td>
         <td>
            <p>44740</p>
         </td>
         <td>
            <p><a href="https://www.lowes.com/pd/Sigma-Electric-ProConnex-3-8-in-Snap-in-Connector-Conduit-Fitting/3151125">www.lowes.com</a></p>
         </td>
      </tr>
      <tr>
         <td>
            <p>Junction box</p>
         </td>
         <td>
            <p>1</p>
         </td>
         <td>
            <p>Lowes</p>
         </td>
         <td>
            <p>10029</p>
         </td>
         <td>
            <p><a href="[https://www.lowes.com/pd/CARLON-Gray-Weatherproof-Pvc-Junction-Box/1000975650](https://www.lowes.com/pd/CARLON-Gray-Weatherproof-Pvc-Junction-Box/1000975650)">www.lowes.com</a></p>
         </td>
      </tr>
      <tr>
         <td>
            <p>3D printed cuvette holder</p>
         </td>
         <td>
            <p>1</p>
         </td>
         <td>&nbsp;</td>
         <td>&nbsp;</td>
         <td>&nbsp;</td>
      </tr>
      <tr>
         <td>
            <p>Multimeter</p>
         </td>
         <td>
            <p>1</p>
         </td>
         <td>
            <p>CEN-TECH</p>
         </td>
         <td>
            <p>61593/P37772</p>
         </td>
         <td>
            <p><a href="https://www.harborfreight.com/11-function-digital-multimeter-with-audible-continuity-61593.html">www.harborfreight.com</a></p>
         </td>
      </tr>
      <tr>
         <td>
            <p>1KV DC Power supply (e.g., Bio-Rad PowerPac 1000)</p>
         </td>
         <td>
            <p>1</p>
         </td>
         <td>
            <p>Bio-Rad (or other)</p>
         </td>
         <td>&nbsp;</td>
         <td>&nbsp;</td>
      </tr>
      <tr>
         <td>
            <p>Red banana plug test lead - 24 inch - 15A</p>
         </td>
         <td>
            <p>1</p>
         </td>
         <td>
            <p>Mouser</p>
         </td>
         <td>
            <p>B-24-2</p>
         </td>
         <td>
            <p><a href="https://www.mouser.com/ProductDetail/Pomona-Electronics/B-24-2?qs=Jz4yJwmcGUolf%2Ft6R9QPRg%3D%3D">www.mouser.com</a></p>
         </td>
      </tr>
      <tr>
         <td>
            <p>Black banana plug test lead - 24 inch</p>
         </td>
         <td>
            <p>1</p>
         </td>
         <td>
            <p>Mouser</p>
         </td>
         <td>
            <p>B-24-0</p>
         </td>
         <td>
            <p><a href="https://www.mouser.com/ProductDetail/Pomona-Electronics/B-24-0?qs=sGAEpiMZZMvdy8WAlGWLcB2mHTMXCqDa">www.mouser.com</a></p>
         </td>
      </tr>
      <tr>
         <td>
            <p>Horizontal Gel Electrophoresis System</p>
         </td>
         <td>
            <p>1</p>
         </td>
         <td>
            <p>Thermo Fisher Scientific</p>
         </td>
         <td>
            <p>FB-SB-710 (or similar)</p>
         </td>
         <td>
            <p><a href="https://www.fishersci.com/shop/products/fisherbiotech-horizontal-electrophoresis-systems-minigel-system-7-x-10cm-gel-size/fbsb710">www.fishersci.com</a></p>
         </td>
      </tr>
   </tbody>
</table>
<h2>
   <p>Authors</p>
</h2>
<table>
   <thead>
      <tr>
         <td>
            <p><strong>Name</strong></p>
         </td>
         <td>
            <p><strong>E-mail</strong></p>
         </td>
         <td>
            <p><strong>Affiliation</strong></p>
         </td>
         <td>&nbsp;</td>
      </tr>
   </thead>
   <tbody>
      <tr>
         <td>
            <p>Michael Cauchy</p>
         </td>
         <td>
            <p>mcauchy@oswego.edu</p>
         </td>
         <td>
            <p>State University of New York at Oswego</p>
         </td>
         <td>&nbsp;</td>
      </tr>
      <tr>
         <td>
            <p>Ali A. Khan</p>
         </td>
         <td>
            <p>akhan3@oswego.edu</p>
         </td>
         <td>
            <p>State University of New York at Oswego</p>
         </td>
         <td>&nbsp;</td>
      </tr>
      <tr>
         <td>
            <p>Yulia Artemenko</p>
         </td>
         <td>
            <p>yulia.artemenko@oswego.edu</p>
         </td>
         <td>
            <p>State University of New York at Oswego</p>
         </td>
         <td>&nbsp;</td>
      </tr>
      <tr>
         <td>
            <p>David A. Dunn</p>
         </td>
         <td>
            <p>david.dunn@oswego.edu</p>
         </td>
         <td>
            <p>State University of New York at Oswego</p>
         </td>
         <td>&nbsp;</td>
      </tr>
   </tbody>
</table>

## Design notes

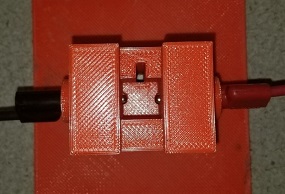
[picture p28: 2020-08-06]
figs/cuv 2.jpg

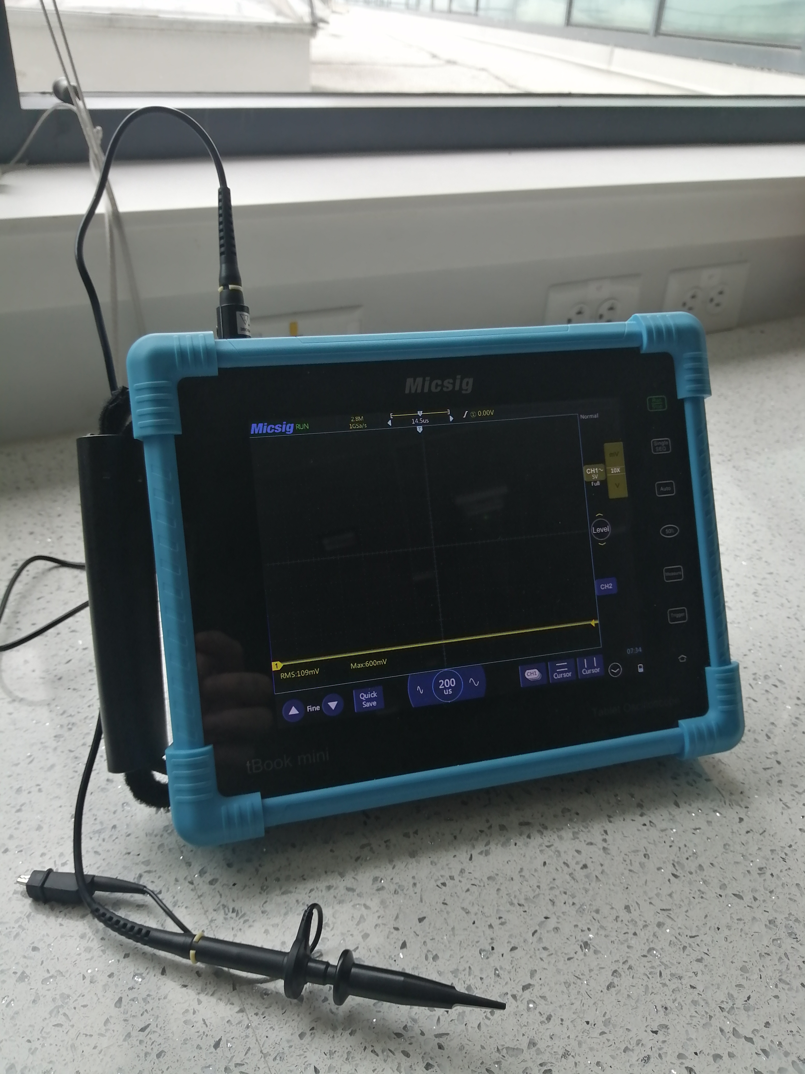
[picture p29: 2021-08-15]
figs/Gen2Micsig.jpg

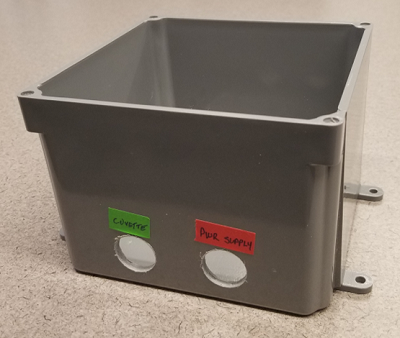
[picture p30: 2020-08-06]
figs/encl 1.png

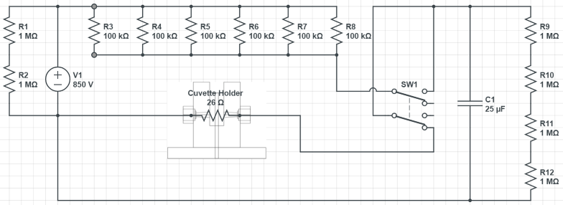
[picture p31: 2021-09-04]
figs/Circuit 2.png

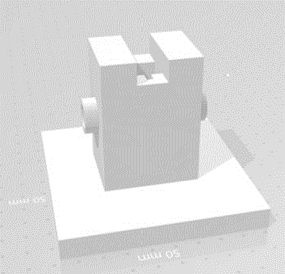
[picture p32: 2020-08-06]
figs/cuv 1.png

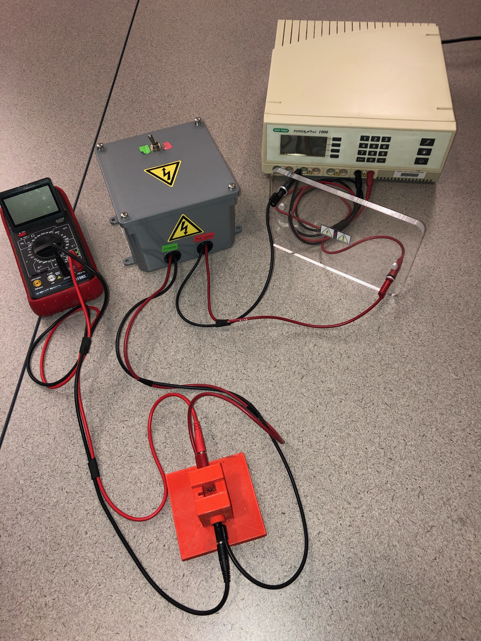
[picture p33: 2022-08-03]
figs/pic 1.png

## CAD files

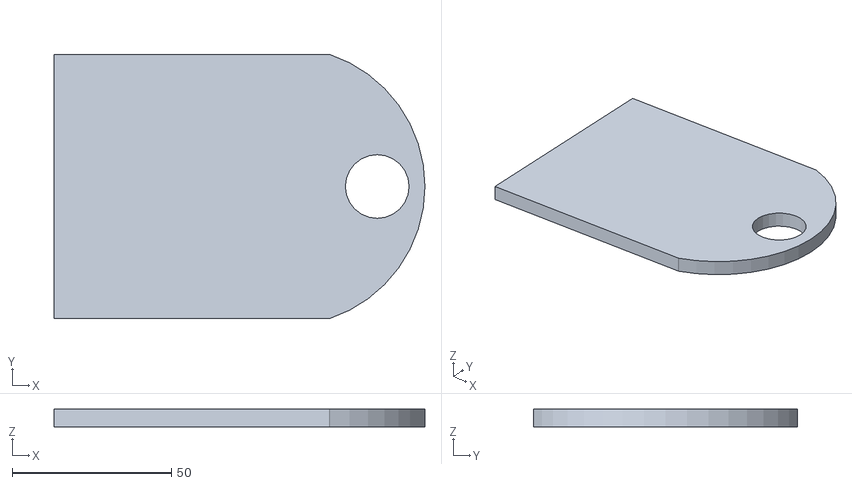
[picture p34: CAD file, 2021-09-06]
Dictyostelium discoideum Electroporator/Enclosure Lid STL.stl
116.5 x 83.0 x 5.58

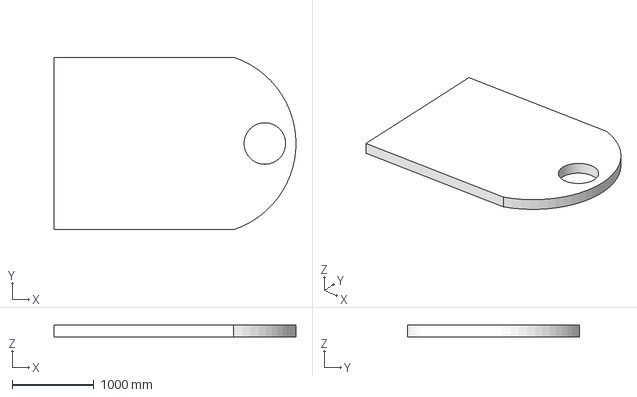
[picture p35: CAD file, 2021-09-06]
Dictyostelium discoideum Electroporator/Enclosure Lid FreeCAD.iges
2959.1 x 2108.2 x 141.7 mm

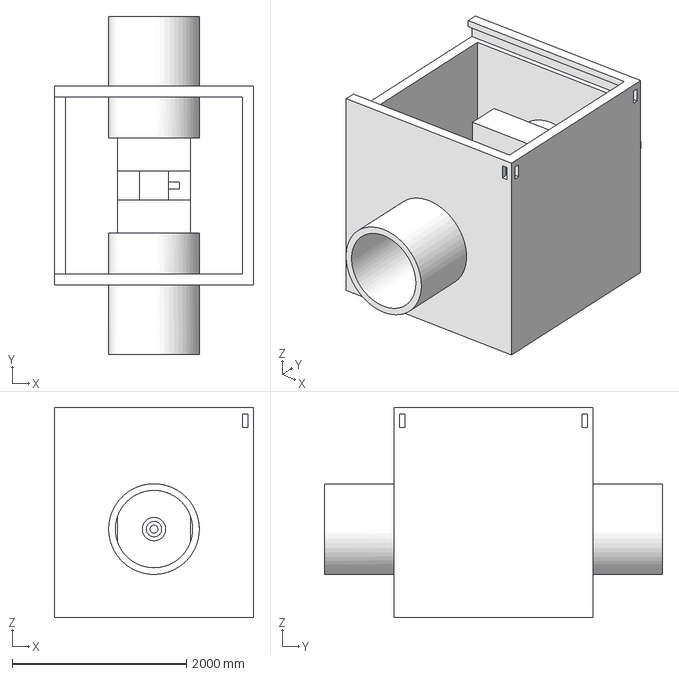
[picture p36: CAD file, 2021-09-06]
Dictyostelium discoideum Electroporator/Enhanced Cuvette Chamber FreeCAD.iges
2286.0 x 3886.2 x 2413.0 mm

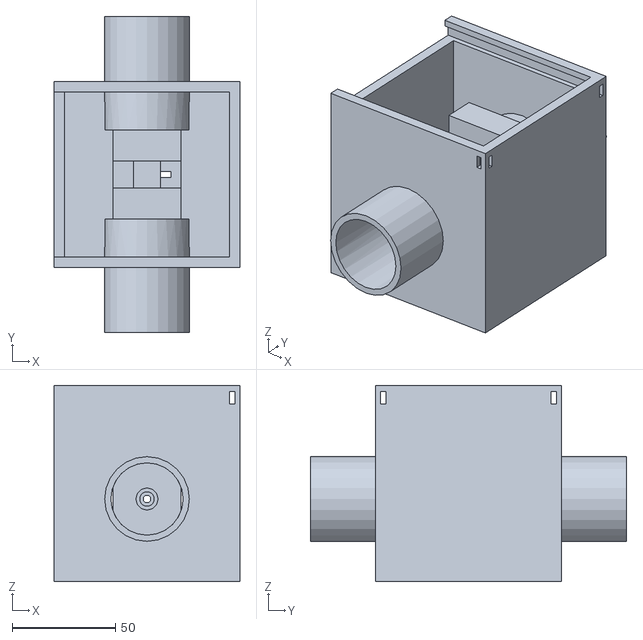
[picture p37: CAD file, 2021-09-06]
Dictyostelium discoideum Electroporator/Enhanced Cuvette Chamber 3DPrintSTL.stl
90.0 x 153.0 x 95.0

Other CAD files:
Dictyostelium discoideum Electroporator/Enclosure Lid CAD.dwg
Dictyostelium discoideum Electroporator/Enhanced Cuvette Chamber CAD.dwg
